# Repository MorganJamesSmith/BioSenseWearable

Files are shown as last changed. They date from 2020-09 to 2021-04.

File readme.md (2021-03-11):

# P21

## Building the Project

The project can be built either with the Makefile in the gcc folder in order to
use the arm-none-eabi-gcc toolchain or with the Segger Embedded Studio project
in the ses folder.

The SES project and Makefile are both configured to build the project for the
nRF52840 Dongle (PCA10059). The Makefile can also be used to build the project 
for the nRF5284-DK (PCA10056) by setting an additional variable when running
make (`make BOARD=BOARD_PCA10056`).

## Programming the Board

If using the Makefile, the board can be programmed through gdb with
`make debug`, which will start and OpenOCD instance and launch a GDB session
conneted to it. To debug the board with a Black Magic Probe, use the `GDB_FILE`
variable to specify the probe's serial port. For example,
`make debug GDB_FILE=/dev/ttyACM0`.

## Licensing

The folder nRF5_SDK_17.0.0 is third-party code subject to its own licenses.

All other intellectual property in this repository (code, hardware designs,
documentation, etc.) is provided under the BSD-3 clause license (SPDX:
BSD-3-Clause https://spdx.org/licenses/BSD-3-Clause.html).

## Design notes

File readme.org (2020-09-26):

#+title: BioSense21

A university project by Morgan Smith, Samuel Dewan, Tadhg
McDonald-Jensen, and Jason Nyentap.
* Description
A wearable device that would contain a suite of sensors intended to
produce enough information to detect illness before symptoms occur.
* Feature List
** User Interface (do we need one?)
- Vibration Motor (for what?)
- A button (for what?)
- Speaker (for what?)
** Necessary Hardware
- Battery (Lithium Ion)
- Charging circuit
- Accelerometer IMU ($11.07) [[https://www.digikey.ca/en/products/detail/tdk-invensense/ICM-20948/6623535][ICM-20948]]
- Heart rate+oximeter
  ($11.77 [[https://www.digikey.ca/en/products/detail/maxim-integrated/MAX86150EFF/7392247][MAX86150EFF]])
  or
  ($3.64 [[https://www.digikey.ca/en/products/detail/osram-opto-semiconductors-inc/SFH-7050/6137020?s=N4IgTCBcDaIMoDEASACA7ABgKwZAXQF8g][SFH 7050]]) ($7.66 [[https://www.mouser.ca/ProductDetail/Maxim-Integrated/MAX32664GWEC%2bT?qs=%252B6g0mu59x7KPYz%252BeYnJYdg%3D%3D][MAX32664GWEC+T]]) ($10.13 [[https://www.mouser.ca/ProductDetail/Maxim-Integrated/MAX32664GTGC%2b?qs=vmHwEFxEFR%252B4L9bBONurNg%3D%3D][MAX86140ENP+T]])
- Body + Ambient temperature ($1.06 [[https://www.digikey.ca/en/products/detail/microchip-technology/TCN75AVUA713/739451][TCN75AVUA713]])
** Possible Sensors
- air quality ($18.39 [[https://www.digikey.ca/en/products/detail/bosch-sensortec/BME680/7401317][BME680]] includes temperature)
- noise levels (microphone)
- Breath rate sensor (how?) (Pulse oximetry?)
- Pulse oximeter/heart rate
- ECG (AD8232)
- UV exposure ($2.48 [[https://www.digikey.ca/en/products/detail/silicon-labs/SI1133-AA00-GMR/5725927][SI1133-AA00-GMR]])
** Need more research Sensors
- Blood sugar monitor
- Blood pressure monitor
* Similar Projects
** [[https://github.com/estherbm/Open-BioBand][Open-BioBand]]
The code is in Spanish (I think)
License: GPL-3
** [[https://www.pine64.org/pinetime/][PineTime]]
| Soc      | Sensors       | Battery |
|----------+---------------+---------|
| nRF52832 | Heart Rate    | 180 mAh |
|          | Accelerometer |         |

** [[https://www.kickstarter.com/projects/gfw/banglejs-the-hackable-smart-watch/description][Bangle.js]]
- This watch is specifically designed to run javascript, gross.

| Soc      | Sensors    | Battery |
|----------+------------+---------|
| nRF52832 | Heart Rate | 350 mAh |

** [[https://github.com/S-March/smarchWatch_PUBLIC][This random dude who made his own smartwatch]]
- More images here: [[https://imgur.com/a/FSBwD3g][link]]

| Soc     | Sensors       | Battery |
|---------+---------------+---------|
| DA14683 | Accelerometer |         |
* Available drivers and algorithms
https://www.owear.org/open-algorithms
* Studies on early sickness detection
** Currently happening
*** [[https://osher.ucsf.edu/research/current-research-studies/tempredict][TemPredict]]
Using the Oura Ring which is a wearable device that measures heart
rate, inter-beat interval and changes in dermal temperature and is
associated with a smartphone app.
*** [[https://innovations.stanford.edu/wearables][Stanford]]
For iOS users, we support: Fitbit devices, Garmin devices, Samsung Galaxy Watch, Apple Watch, Oura Ring.

For Android users, we support Fitbit devices.
*** [[https://detectstudy.org/][Detect Health Study]]
** Completed
*** [[https://doi.org/10.1016/S2589-7500(19)30222-5][Harnessing wearable device data to improve state-level real-time surveillance of influenza-like illness in the USA: a population-based study]]
References other studies that indicate that increased temperature due
to infection can cause a higher heart rate

Lack of sleep is correlated with an elevated heart rate.

Mentions they would have like to use detection of voice changes or
galvanic skin response to detect stress level to identify
non-infectious causes of elected heart rate.

Heart rate is higher when it's cold and lower when it's warm

Heart rate is higher when you're dehydrated
*** [[https://doi.org/10.1371/journal.pbio.2001402][Digital Health: Tracking Physiomes and Activity Using Wearable Biosensors Reveals Useful Health-Related Information]]
Core temperature decreases during sleep but skin temperature increases

Measurements taken during airline flights differ significantly from
normal measurements

Skin temperature increases from inflammation, and viral disease

Skin temperature increases a lot from Lyme disease

Heart rate increases noticeably when suffering
from Lyme disease or rhinovirus

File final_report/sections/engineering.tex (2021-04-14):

\subsection{Health and Safety}
% {\color{red}
% Using the Health and Safety Guide posted on the course webpage, students will 
% use this section to explain how they addressed the issues of safety and health 
% in the system that they built for their project.
% }
Due to Covid restrictions all electrical work was performed without supervision.  
Since all electrical work uses USB power of 5V no risk of serious injury was possible.
To mitigate risk of shock, it was ensured that work area is clear and that there are no live wires exposed while the board is connected to the power source.
All soldering was performed within reasonable safety guidelines.

\subsection{Engineering Professionalism}
% {\color{red}
% Using their course experience of ECOR 4995 Professional Practice, students 
% should demonstrate how their professional responsibilities were met by the 
% goals of their project and/or during the performance of their project.
% }
% Several aspects of the project were affected by engineering practices
In order to ensure user privacy is maintained, the data collected by the device is only stored locally and
can only be offloaded by USB or SD card (physical access) or over bluetooth using standard bluetooth encryption.
The device is enclosed in a way that ensures that electrical shock is not possible under normal operation.
The bluetooth module we are using is industry canada certified to be safe to use.

\subsection{Project Management}
% {\color{red}
% One of the goals of the engineering project is real experience in working on a 
% long-term team project. Students should explain what project management 
% techniques or processes were used to coordinate, manage and perform their project.
% }
Each member of the team was, due to individual passions, interested in different
aspects of the project, thus division of tasks was organic and did not require a leader or dictating division of work.
Good communication over instant messaging and occasional meetings to discuss updates and re-evaluating
task assignment ensured fair distribution and completion of work.
Though we had created a timeline,
due to underestimating the amount of time certain tasks would take to
accomplish, the timeline had to be pushed back. Working with a group and
deadlines enabled the development of time management skills.

\subsection{Justification of Suitability for Degree Program}

All team members are studying Computer Systems Engineering.  This program
teaches hardware, software, and the intersection between them.  This gave us a
strong foundation for developing our project as an embedded system.  We
applied what we have learned in ELEC and SYSC courses related to embedded
processors to develop our own hardware platform.  This required us to
exercise our electronic circuit analysis skills using concepts like Ohms law or
Kirchhoff’s voltage and current laws to make sure our electronics work
properly.  In order to connect all of our sensors and interfaces to the
embedded processor we used what we have learned about microcontroller
peripherals such as UART, I2C, SPI, GPIO, and timer modules.  In addition to 
creating our own hardware, we wrote software that runs on the embedded processor
to control the device.  The C programming language was used to do this, and we 
applied much of the knowledge and techniques learned from several SYSC courses.  
This includes concepts like interrupts, managing multiple tasks and events, 
using the hardware features of the embedded processor and more.  Some of the
non-technical courses included in the Computer Systems Engineering program have 
also proved useful for managing the project and writing reports. 
% this final sentence is weird.
Since we 
have applied large portions of the knowledge gained from our studies to
our project we believe the project is relevant to what we have studied and 
relevant to our degree program.
% due to the previous courses taken by members of the group, we feel as though we can apply our theoretical knowledge to a practical application more efficiently

\subsection{Individual Contributions}
In this section, the contributions of each group member to the project are
presented. The contributions are divided into those related to the project 
itself, and secondly those related to the writing of this report.

\subsubsection{Project Contributions}
The list below details the contributions of each group member towards the
implementation and testing of the project. In cases where components were 
shared by group members, percentages are given.

\begin{itemize}
    \item Hardware component research and selection - Jason 50\%, Sam 50\%
    \item Electronic prototyping - Jason
    \item Schematic capture - Jason 80\%, Sam 20\%
    \item PCB layout - Jason
    \item PCB assembly - Sam
    \item Hardware Debugging - Sam
    \item Bill of materials and Purchasing - Sam
    \item Command line interface - Sam
    \item USB driver - Sam
    \item Analog interface code - Sam
    \item ICM 20948 IMU driver - Sam
    \item Data logging and file systems - Sam
    \item Bluetooth driver - Jason
    \item Bluetooth interface for companion software - Jason 60\%, Tadhg 40\%
    \item Companion app CLI interactions and usb connection - Tadhg
    \item log file parsing and plotting - Tadhg
    \item Companion app automated testing - Tadhg
    \item Enclosure design - Morgan
    \item Enclosure fabrication - Morgan
    \item MAX86150 PPG/ECG driver - Morgan
    \item Guix package - Morgan
    \item SI1133 UV light sensor driver - Tadhg
\end{itemize}

\subsubsection{Report Contributions}
The list below details the contributions of each group member towards this final
report. In cases where sections were shared by group members, percentages are
given.

\begin{itemize}
    \item 0 Abstract - Morgan
    \item 1.0 Introduction - Morgan 60\%, Jason 30\%, Tadhg 10\%
    \item 1.1 Motivation - Morgan 50\%, Tadhg 50\%
    \item 1.2 Problem Statement - Jason
    \item 1.3 Solution - Tadhg
    \item 1.4 Accomplishments - Morgan
    \item 1.5 Report Structure - Tadhg
    \item 2.1 Health and Safety - Tadhg
    \item 2.2 Engineering Professionalism - Tadhg
    \item 2.3 Project Management - Tadhg
    \item 2.4 Justification of Suitability for Degree Program - Jason
    \item 3 State of the Art - Jason
    \item 4.1 Component Selection - Sam 80\%, Jason 20\%
    \item 4.2 Schematic - Jason
    \item 4.3 PCB Layout - Jason
    \item 4.4 Enclosure - Morgan
    \item 5 Software Implementation Description - Sam
    \item 5.4.1 USB - Sam
    \item 5.4.2 Bluetooth - Jason
    \item 5.4.3 Heart Rate - Morgan
    \item 6.1 Integration Testing - Sam
    \item 6.2 Performance Measurements - Sam
    \item 6.3 Power Measurements - Jason
    \item 6.4 Companion App Testing - Tadhg
    \item 6.5 Physical Dimensions - Morgan
    \item 6.6 Cost - Sam
    \item 7.1.1 Power and Battery Design Challenges - Jason
    \item 7.1.2 Assembly and Parts Availability Challenges - Sam
    \item 7.2.1 Toolchain and nRF5 SDK Challenges - Sam
    \item 7.2.2 USB and Bluetooth Integration Challenges - Jason
    \item 8 Timeline - Morgan
    \item 9 Conclusion - Tadhg
\end{itemize}

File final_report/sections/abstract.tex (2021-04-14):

Early detection of illness could limit the spread of infection, save lives, and
save money.  One possible method of early detection is to continuously measure
someones physiological state.  Here we detail our creation of such a continuous
biometric measurement device.  The device is in the form factor of a watch and
contains sensors to measure skin temperature, ambient temperature, motion, 
heart rate, pulse oximetry, and UV light. The software drivers for UV light,
heart rate and pulse oximetry were not completed in time so data is only
recorded from motion and temperature sensors. The PCB also supports an air
quality sensor which was never populated due to a lack of availability.
The device is powered by a lithium ion battery that is charged
through a USB port and lasts two days of normal operation.  
The total cost of the unit is \costofboard.  Sensor data can be
obtained through the SD card, USB port, or Bluetooth by using the appropriate companion
software.  The companion software can then produce graphs to display the output
of the sensors.  The focus of this solution is on the collection of biometrics
and making them available for analysis.  No attempt was made to perform medical
analysis or give clinical diagnosis from the collected biometrics.  Our
intention was to design an open source system so that those applications could be
integrated with or built on top of the work we have done for this project.

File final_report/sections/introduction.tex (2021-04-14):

This report details the design and creation of a continuous biometric measurement
device costing a total of \costofboard. This device takes measurements from the user
and prepares them for analysis to detect illness or otherwise track well being.

Traditionally, people only seek treatment for ailments after they start
experiencing symptoms; however, it is often desirable to take action before
symptoms appear.  One solution to catch illness earlier could be to monitor a
person's physiological state using various sensors and take action when the
state falls outside of a known healthy state.

Wearables are capable of revealing personal daily physiological cycles with
respect to skin temperature, and heart rate with high accuracy 
\cite{Schuurmans2020}. By comparing a person's current physiological
state with the expected state, it is possible to predict illness with greater
sensitivity than a self diagnosis \cite{POON2014543}. 
One specific example is a study was able to detect a
period of inflammation (confirmed by a medical high-sensitivity C-reactive
protein test) using a participant's heart rate even though the participant
themselves experienced no symptoms \cite{Wearable-tracking2017}.  The same
study even helped a participant get treatment of Lyme disease before the
``Bull's eye'' rash appeared (a common symptom during the early stages of Lyme
disease) by detecting an abnormality in their SpO\textsubscript{2} levels.

Wearable data can also be used to detect group illness rates.  By using heart
rate data and sleep data from fitbit devices and cross referencing that data
with the Centers for Disease Control and Prevention's (CDC) Influenza Like
Illness (ILI) data, a study was able to predict illness 6.3\% to 32.9\% better
than previous methods \cite{Radin2020}.

A survey on health sensing wearables showed that physiological data collected 
over longer periods of time can be useful for gait analysis and activity 
quantification, among other things \cite{Song2014}. Gait analysis is useful for 
patient mobility evaluation in hospitals, can help diagnose some diseases, and 
can also be used as a more general indicator of health \cite{Song2014}. Activity
quantification is import to aid patients undergoing rehabilitation \cite{Song2014}.

Wearables can also detect more immediate dangers to someone's health like a
heart attack \cite{heart-attack}, a fall \cite{Khojasteh_2018}, or dangerously
low or high heart rates.  This information could be used to alert emergency
services to save lives.

In addition to collecting physiological data, many wearables can also measure
environmental data and positional data \cite{Seneviratne2017}. This data has 
proven useful in dangerous work environments such as those commonly 
found in the mining industry \cite{Mardonova2018}. Air quality information can
help miners avoid inhaling hazardous gasses or respirable silica dust 
\cite{Mardonova2018}. Some wearables will even detect when equipment operators
are becoming sleepy and warn them that it is no longer safe to continue working
\cite{Mardonova2018}. In the construction industry, there is a high rate of 
severe contact injuries \cite{Awolusi2018}. The use of location data can help 
reduce these contact injuries by preventing workers from entering dangerous 
areas or coming into contact with equipment \cite{Awolusi2018}. Wearable devices
capable of measuring both physiological data and elevation can be used to detect
altitude sickness, which can occur when unacclimated individuals experience sudden 
changes in elevation \cite{Muza2018}. These sudden changes in elevation are 
possible while driving, riding a train, flying, or taking a cable car up a mountain 
\cite{Muza2018}.

\subsection{Motivation}

Despite all of the advances in medical technology, a cure for diseases and
allowing humans to live longer are ever present goals for scientists and 
doctors alike.  Often wide spread diseases we have not prepared for can occur in
society.  COVID-19 is a pandemic that
has, at the time of writing, claimed an estimated 3 million lives globally
\cite{johns-hopkins-corona-chan}, and continues to infect more people every
day.  In 2007 it was estimated that the total cost of occupational illnesses
among civilians in the United States was \$58 billion \cite{Leigh2011}.
Slowing the spread of disease could save lives and save money.

One method of limiting the spread of disease is early diagnosis.  This would
allow individuals who are aware they are ill to take measures to reduce the
spread of their illness, even before symptoms manifest.  This will be
particularly useful for healthcare providers who work with high risk
individuals, since identifying symptoms early has the highest efficiency for
protecting others.

By creating a personal physiological profile and constantly
comparing the user's current physiological state to it, illness can be detected
early.  The motivation for our project is to create a device capable of measuring 
enough of the user's current physiological state to predict illness.  This is done 
in the hope that it could be used to slow the spread of illness's and, to speed
recovery from illness's by starting treatment earlier.

\subsection{Problem Statement}

One way to facilitate early diagnosis is to periodically measure biometrics on 
patients and make clinical diagnoses based on patterns or changes in the 
measurements. A convenient and low-cost method to collect and log biometric data 
is needed in order to make the potential benefits of the technology available to 
a large number of people. Wearable devices are well suited to this application 
because they have continuous access to the user’s biometric data as long as the 
device is being worn, and they do not require any input from the user to perform 
most, if not all, measurements. This means that a wearable device can take as 
many measurements as it needs, whenever it needs to, in order to create useful 
data logs that describe the user’s biometrics and perhaps their environment at 
the time the measurements were taken.  This information may then be used to 
detect abnormalities in the user’s physiology and could be used to aid in the 
early detection of illness. The objective of this project therefore, is to 
create a wearable device that can measure a variety of critical health metrics 
including skin temperature and heart rate.

\subsection{Solution}

The solution provided by this project is a wrist mounted wearable health 
monitoring device. The device provides a sensor platform that is suitable for 
early detection of disease. The included sensors can measure skin temperature, 
ambient temperature, motion, heart rate, pulse oximetry, UV light, and air quality.  
The electronic components fit into a comfortable, wearable 3D printed plastic enclosure.
The device is powered by a lithium polymer battery which can be recharged
through the USB-C connector.  The final cost of the full device ends up being \costofboard.

The wearable device has limited user interfaces consisting of an indicator
LED for power, notifications, and debugging. It also features a power button
to turn the device on and off. The main interactions with the device occur 
through a companion software that connects to the device through Bluetooth or 
USB. It is limited to simply receiving and decoding data received from the 
wearable device, and exporting it in an analyzable format such as a csv or json 
file.

The device stores the collected sensor information to a micro SD card
in the device which is then read back when requested via the companion software.
The SD card is replaceable, and the capacity of the card used will dictate
how long the device can record data before needing to off load to the companion
software.

The focus of this solution is on the collection of biometrics and making them
available for analysis. No attempt was made to perform medical analysis
or give clinical diagnosis from the collected biometrics. Our intention was to
design the system so that those applications could be integrated with or built
on top of the work we have done for this project.

%Should this be in a reflection or something? Not really part of a solution,
%it is a disclaimer.

%In order to reduce development cost and complexity, the hardware component of
%the project uses sensors that are readily available from online sources, and 
%that can be assembled on a PCB by hand relatively easily. As a result the 
%selection of sensors may be more limited or lower quality than what is possible 
%if options that are made to order, or only available in large quantities had been
%explored.  The use of parts that can be soldered to a PCB without paying for
%the services of an advanced manufacturing facility also resulted in the final 
%hardware design being larger than it would have been otherwise.

\subsection{Accomplishments}

Our team successfully created a wrist mounted wearable health monitoring device
that is capable of measuring skin temperature, ambient temperature, and motion.
The hardware for heart rate, pulse oximetry, and UV light sensors are in place
however the software drivers were not completed in time. 
The air quality sensor was never available so the driver was not started and was
never populated on the PCB. The hardware is fully functional and correctly
connects all the selected components together.  The software is able to connect
the device to companion software located on a separate device using Bluetooth
and USB.  We are able to log motion and temperature sensor to the SD Card.

\subsection{Report Structure}
Subsequent sections of this
report cover the hardware and software design of the project in detail, as well
as discuss some of the challenges that were faced in pursuing the solution
outlined here. Information regarding the tests performed on the final project
are also detailed in this report, and a series of appendices are included with
visuals to show some interesting parts of the design and what the final product
looks like.

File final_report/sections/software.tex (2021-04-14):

We have split our firmware into a number of separate modules, as shown in figure
\ref{fig:fw_block_diag}. All of the drivers for microcontroller peripherals
such as serial interfaces and the ADC are provided by the nRF52 SDK, which is a
library provided by Nordic Semiconductor, the manufacturer of the nRF52840
microcontroller we are using. We are also using some higher level components
from the nRF52 SDK such as the USB CDC-ACM stack, a FAT32 filesystem driver and
Nordic's soft device S140 which is a Bluetooth LE peripheral stack.

These third party components are be used by the software we wrote ourselves
which includes the drivers for all of our sensors (IMU, optical heart rate
sensor, air quality sensor and UV light sensor) as well as the signal processing
code required to derive a heart rate from the raw data we receive from our
optical heart rate sensor.

At the application layer we have three modules. Our data logging service is
responsible for most of the operation of our device and continually collects
and logs sensor data. The Bluetooth data transfer service facilitates accessing
the logged data over a Bluetooth interface. Our debugging interface exposes our
firmware functionality over a USB serial interface so that integration tests can
be run on the microcontroller.

\begin{figure}[!htb]
\centering
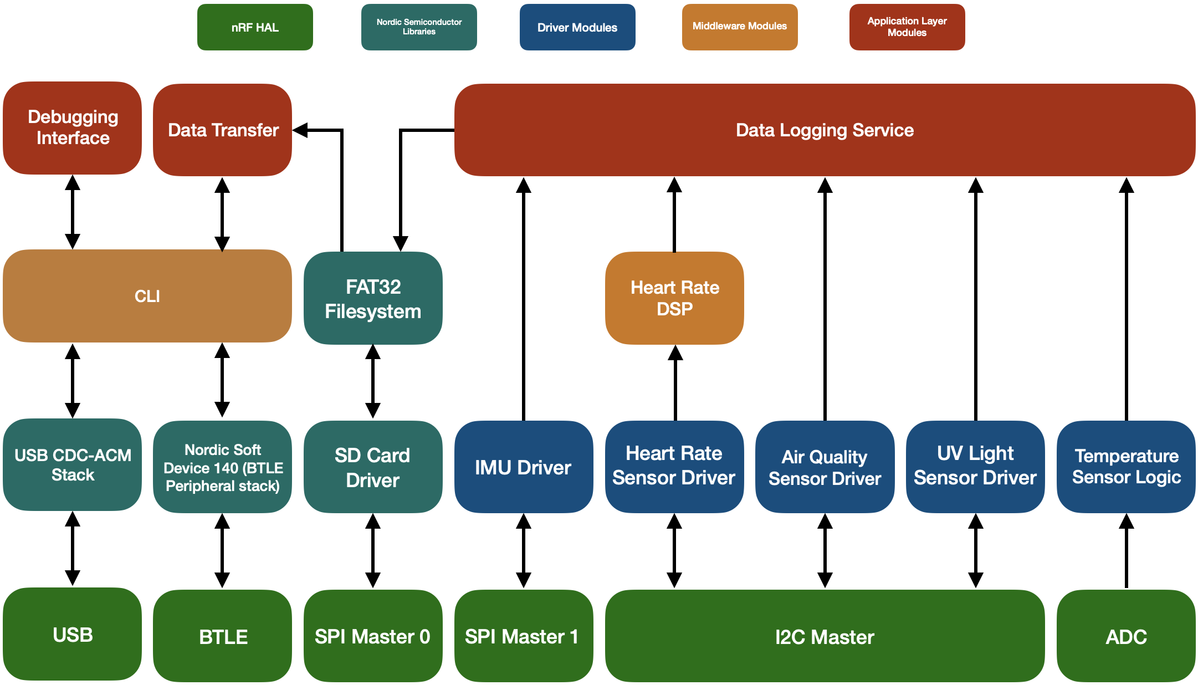
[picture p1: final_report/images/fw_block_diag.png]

\caption{Firmware block diagram.}
\label{fig:fw_block_diag}
\end{figure}

\subsection{Super Loop}

We chose to use a super loop architecture for our firmware because we predicted
that the approach would be sufficient for our needs and would be easier for us
to implement then making use of a realtime operating system. Our firmware
consists of an initialization section followed by an infinite main loop.

Our code is separated in to a number of software modules (as shown in figure
\ref{fig:fw_block_diag}). The software modules that we wrote have an
initialization function which is called once on system startup. Some of our
firmware modules are entirely interrupt based, but many have a service function
which is run in each iteration of the main loop.

Figure \ref{fig:fw_flow} shows the flow of our firmware. We start with a number
of initialization tasks before starting to loop through the service functions
for our modules. Each service function will check if there is any work to be
done for a specific module and start tasks that are ready to begin. After
each iteration of the main loop the wait for interrupt instruction is used to
cause the processor to enter a sleep mode until an interrupt occurs. We have a
timer configured to generate interrupts every millisecond to increment a count
which is used as a time reference throughout the firmware, because of this the
processor will sleep for at most one millisecond at a time.

\begin{figure}[!htb]
\centering
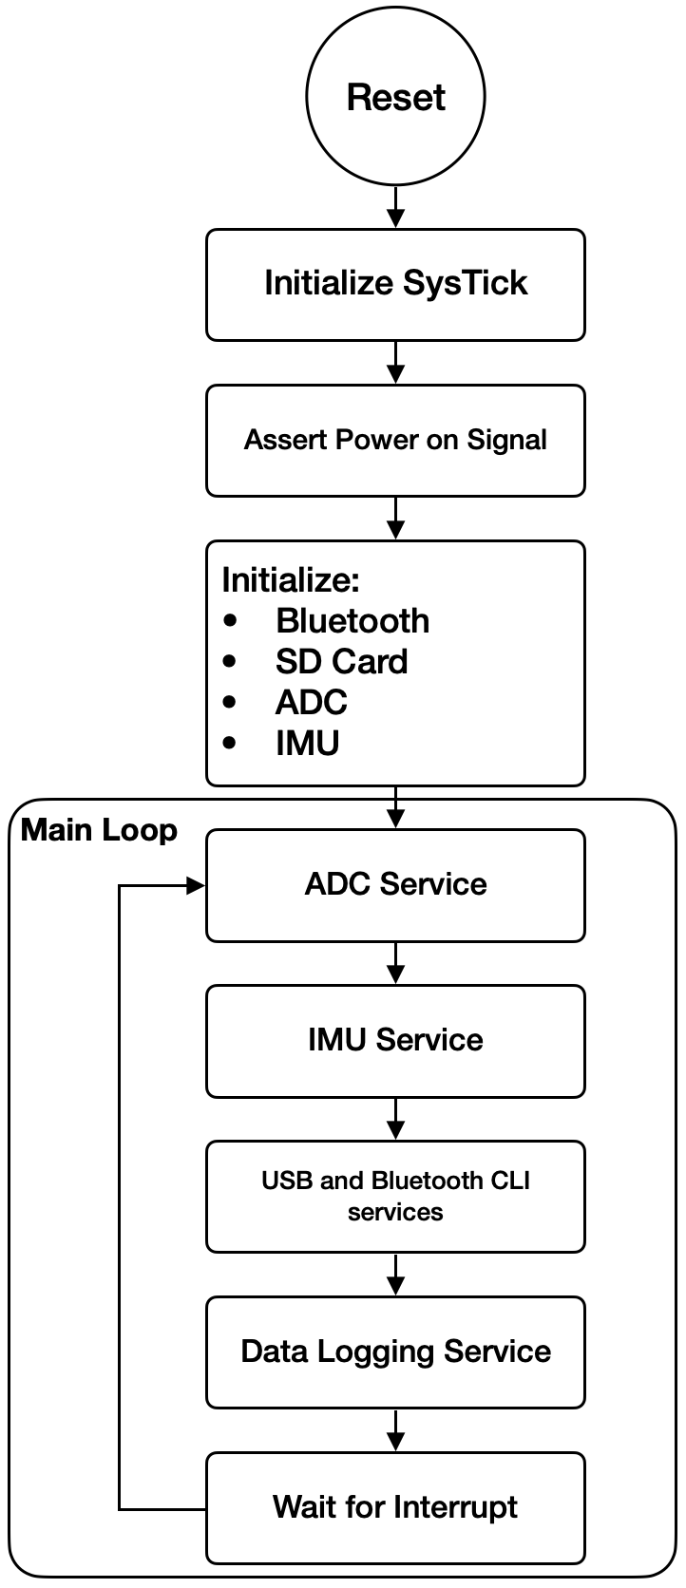
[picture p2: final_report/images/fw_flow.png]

\caption{Firmware flow chart.}
\label{fig:fw_flow}
\end{figure}

The super loop architecture is a cooperative multitasking system. This makes it
important that the service functions which are called in the main loop do not
block for long periods. If a service function was to block it would prevent the
other software modules on the system from operating correctly. In order to meet
this requirement our service functions are written as state machines. Modules
keep track of their current state and are able to determine what, if anything,
needs to be done in each iteration of the main loop based on their state.

We were not able to completely avoid blocking in the main loop because of our
use of a third party FAT filesystem implementation. The filesystem implementation
blocks while writing to the SD card. The performance implication of this are
discussed in section \ref{subsec:testing-data-logging}.

\subsection{Interrupts and Bluetooth Soft Device}

Our firmware makes use of a bluetooth stack provided by Nordic Semiconductor
know as the S140 Soft Device. This "soft device" is distributed as a binary
blob which is flashed to the microcontroller separately from the application
software. The soft device takes ownership of number of microcontroller
peripherals including the radio hardware, clock and power management peripherals,
multiple timers, non-volatile memory controller and cryptography accelerators.
The soft device schedules itself independently of the application using one of
the microcontroller's real time clocks and application software interacts with
the soft device using supervisor calls.

All interrupts are received by a piece of code called the master boot record
(MBR). The MBR then forwards them to the soft device if there is one installed
on the microcontroller. The soft device uses some interrupts for its own
purposes, and interrupts which the soft device does not use are forwarded to the
application. Nordic Semiconductor specifies that this forwarding process adds
less than three microseconds of latency to peripheral interrupts which are to
handled by the application.

Figure \ref{fig:fw_int_prio} shows the interrupt priorities used in our system.
The priority levels shown in red are reserved by the soft device bluetooth
stack, those shown in blue are available for use by application software. The
soft device uses the highest interrupt priority level for its timing critical
interrupts. The second highest interrupt priority level is reserved for the
soft device's peripheral access control fault handler so that the soft device
can safely handle any faults which are caused by application interrupts. The
soft device also used priority level four for API calls and processing tasks
that are not time critical.

\begin{figure}[!htb]
\centering
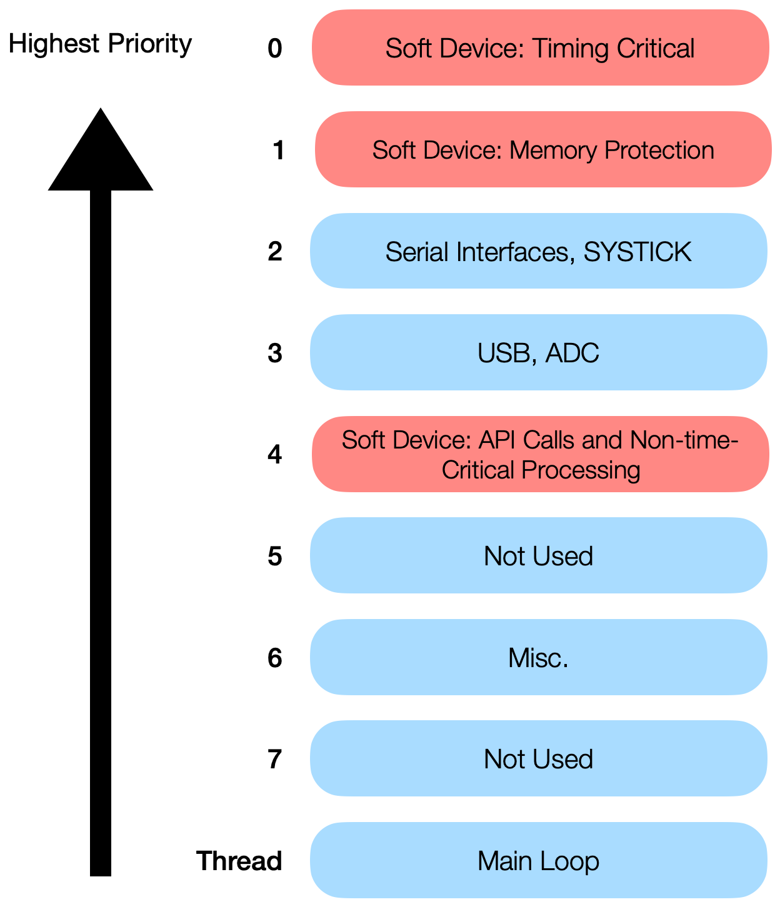
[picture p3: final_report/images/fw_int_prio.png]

\caption{Interrupt priorities.}
\label{fig:fw_int_prio}
\end{figure}

Most of our application interrupts are configured at priority levels two and
three. Our interrupts are grouped into SysTick and and serial interface
interrupts at priority two and USB and ADC interrupts at priority three.

The priority two interrupts are those which we expect to be very short. The
SysTick interrupt is at a high priority to avoid help avoid jitter in our system
time and the serial interrupts are placed at priority two to achieve the best
possible serial interface performance.

\subsection{Data Logging}

The core of our firmware is the data logging service. Sensor drivers push data
to this software module which is buffered and then later stored to the SD card
using the FAT filesystem. The data logging module has two 512 byte buffers. The
module fills one buffer, then writes it to the SD card as it begins to fill the
other.

Figure \ref{fig:fw_data_flow} illustrates the flow of data through the data
logging service. Each sensor driver pushes data to the data logging service at a
rate selected based on the type of data that the sensor produces. Every sample
of sensor data is wrapped in a header that indicates the current system time
when the value was collected, the type of data, and the length of the data.
The resulting packet is then added to the data logging service buffer. Approximately
once per second the data logging buffer will be written to the SD card using the
filesystem driver.

\begin{figure}[!htb]
\centering
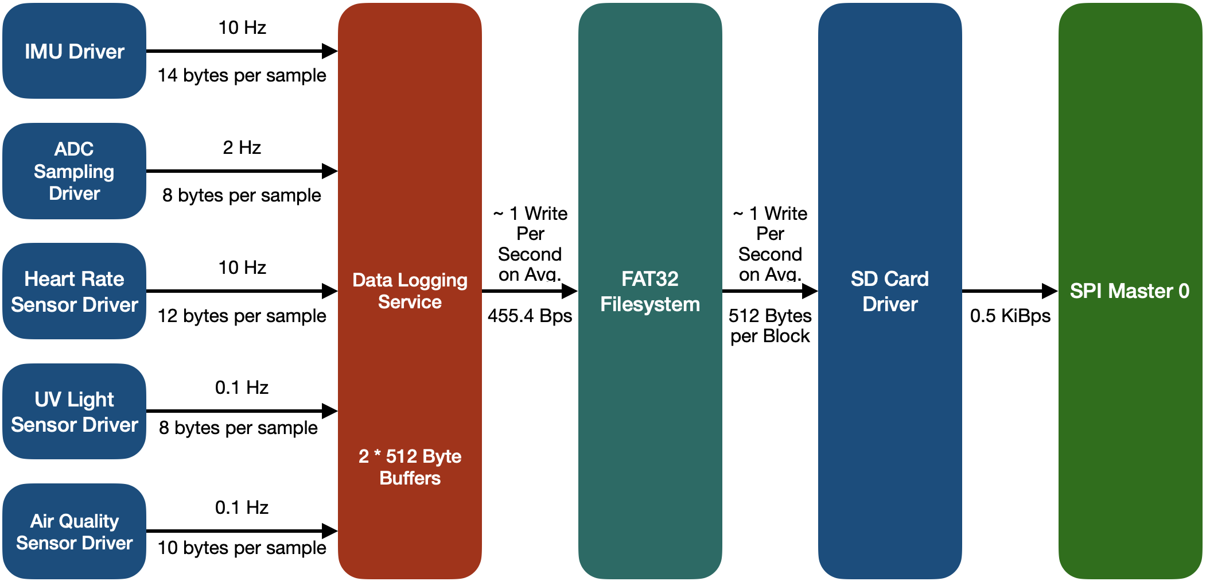
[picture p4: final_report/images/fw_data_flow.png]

\caption{Data flow.}
\label{fig:fw_data_flow}
\end{figure}

\subsection{Drivers}

\subsubsection{USB}

The USB serial interface software module provides a simple abstraction over the
nRF5 SDK's USB communications device class abstract communications model
(CDC-ACM) driver which allows for serial port emulation. The USB serial module
maintains circular buffers for input and output and provides a variety of
functions for reading from and writing to the buffers. The output buffer can be
written to in a blocking or non-blocking fashion. The input buffer can be read
character by character, in blocks, or by line with a selectable delimiter.

\subsubsection{Bluetooth}

The design goal for the Bluetooth driver was to have it behave like a serial
port in the same fashion that USB CDC does. Our intention in doing this was to 
simplify the design of the companion software as well as the command line 
interface present on the microcontroller. This goal was fully achieved 
on the microcontroller side of the communication link. The software interface for 
Bluetooth was made identical to USB so that they can be used interchangeably 
without additional complications. On the PC side where the companion software
runs the solution was not as elegant. We had hoped to find a way to make the
Bluetooth connection appear as a serial port so it could be used interchangeably
with the USB CDC connection, but a method to do this was not found. It likely
could be done by writing custom drivers, but this was outside the scope of the
project. Instead, a cross platform Python library was used to establish the
Bluetooth connection to the device and communicate with it as you normally
would with a Bluetooth device.

The device uses Bluetooth Low Energy, which works by advertising
available services to other nearby devices. Each service may offer a number
of characteristics that can be read only, write only, read-write, and have 
several other options such as notifying a connected device when a characteristic
value changes. The Bluetooth Low Energy specification includes descriptions of several
standard services and their characteristics, but none of these could be used to
to achieve the serial port-like behaviour needed for this project. A custom
serial port service included with the Nordic SDK was used instead. This service
has two characteristics, one named TX and one named RX. The RX characteristic is
write only and is used to send data to the device. The TX characteristic is
written to only by the device and has notifications enabled. If a connected device
wants to receive data then it must subscribe to the notifications of the TX 
characteristic. This solution worked out quite well, although it has a low 
throughput in comparison to USB. The fact that each notification packet can only 
hold approximately 20 bytes and must be acknowledged before the next one is 
sent likely contributes to the low throughput significantly. It was not expected
that Bluetooth Low Energy would be very fast however, since it is optimized for 
power consumption instead of speed. This trade-off is well suited to this project 
because it is battery powered.

\subsubsection{Heart Rate Sensor}

Our heart rate driver is based on an open source implementation written in
C++ \cite{max86150-ardino}. Since the SDK we are using falls under the nRF5
Nordic License, only software that is compatible with this license can be
integrated into the project. The open source C++ heart rate driver is under the
expat license so we are free to use it as long as the copyright notice is
maintained. Unfortunately, not all useful open source software was licensed in
a way compatible with the SDK license. In particular, it would have been ideal
to reuse an algorithm to convert raw PPG data to beats per minute, however the
available algorithm was licensed with the Lesser GNU Public
License \cite{wasp-os} which is incompatible with the SDK license.

\subsubsection{Inertial Measurement Unit}

Our driver for the ICM 20948 IMU is written from scratch. The driver is a finite
state machine that makes use of the nRF5 SDK's SPI driver. The state machine
controls the process of initializing the sensor and of periodically taking
readings, which are then handed off to the data logging service to be recorded.

A simplified state diagram for the IMU driver is shown in figure
\ref{fig:fw_imu_fsm}.

\begin{figure}[!htb]
\centering
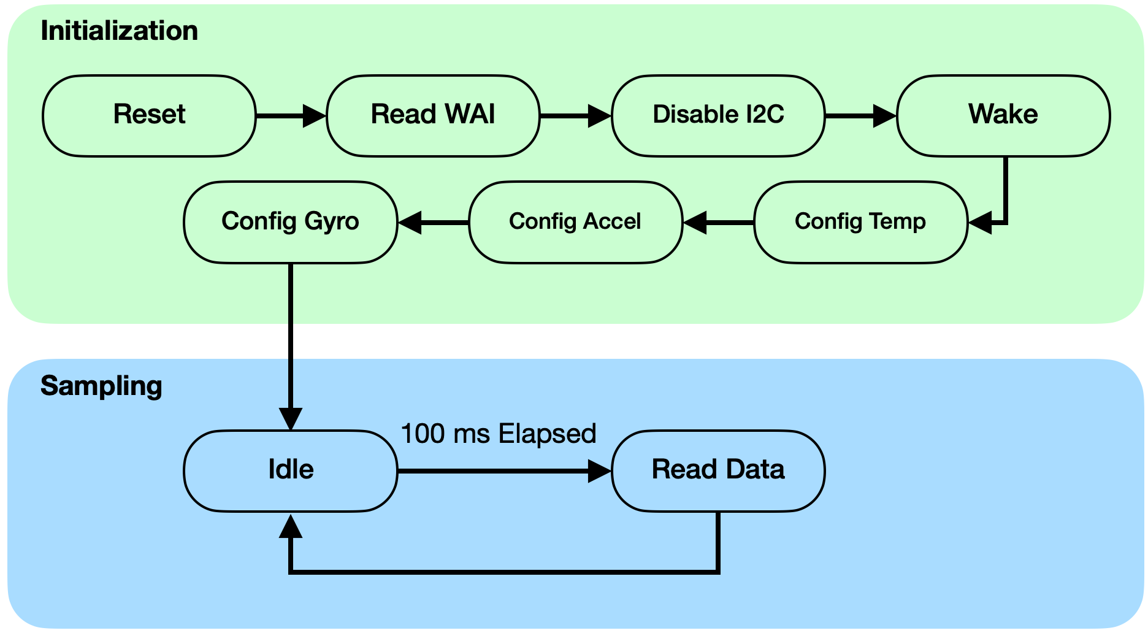
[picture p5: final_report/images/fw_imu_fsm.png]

\caption{IMU driver state machine.}
\label{fig:fw_imu_fsm}
\end{figure}

\subsection{Command Line Interface}

Our firmware provides a command line interface (CLI) which is available via the
USB or bluetooth serial interfaces. This command line interface is used for
debugging, testing and for interaction with the companion app. Our CLI
abstraction provides an identical interface over USB or bluetooth.

The CLI provides a number of commands which are intended for human interaction
including commands for printing out sensor data, accessing profiling information,
writing test messages to the SD card and reading directories and files from the
SD card.

The CLI also has a number of commands which are intended to interact with our
companion software. These functions allow the companion software to read files
from the SD card. The files are written out over the serial interface in
hexadecimal format.

\subsection{Companion App}

The companion app is a desktop application written in python to connect to the device, extract the log data and convert it into a plain text format convenient for further analysis.

Since during development there were a number of things that were likely to change or unknown, the companion software was designed to be highly modular so that each part was isolated for sake of testing and updating.  The flow of data is described by \ref{fig:companion_app}

\begin{figure}[!htb]
    \centering
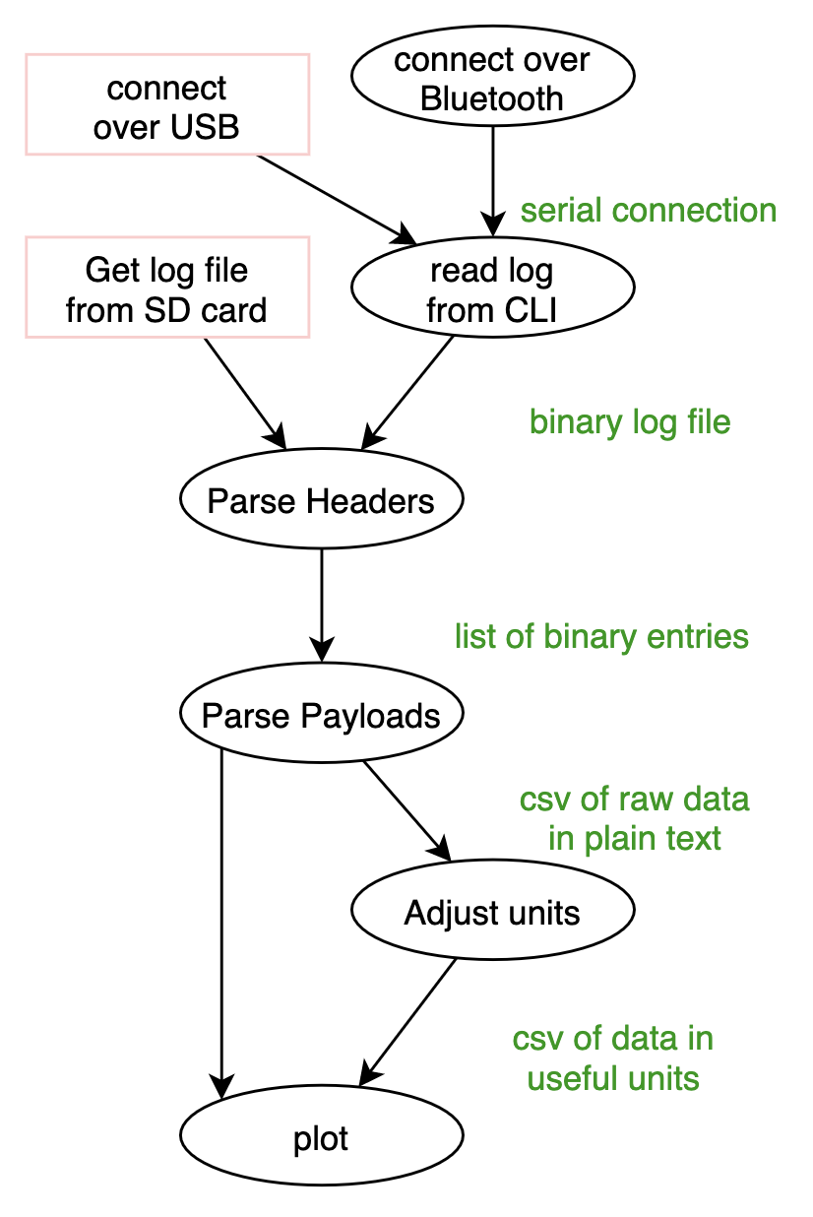
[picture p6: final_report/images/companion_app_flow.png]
    
    \caption{Companion app flow diagram}
    \label{fig:companion_app}
\end{figure}

\subsubsection{Extracting log file}

When the device is connected over USB the companion software can be run to open a serial connection with the device, otherwise the companion software will scan for the device over bluetooth and attempt to pair and connect.  Once a bluetooth connection is established a wrapper is created to emulate the same behaviour as a serial connection so that the CLI communication module can use both connections interchangeably.

The interaction with the CLI consists of sending a time alignment command and using 'hcat' command to read the offset file and log file.  

Since the device does not have time keeping all log entries are recorded with internal timestamps only, the time alignment command creates a log entry matching an internal timestamp with a unix timestamp generated by the companion app.  

The log file consists of binary data blobs with variable length so identifying the boundaries of entries from the middle of the file is impossible without additional context, for this reason a separate file is kept with a list of offsets corresponding to each reset so an option can enable only recording data from a given reset index.

\subsubsection{Parsing log file}

Once the log file is obtained either by extracting it through the CLI interface or by extracting it from the SD card directly, it is converted from a binary format into plain text CSV files for each type of entry.

The module which parses the headers will read the length of each entry's payload and ensure the correct length of bytes is being read.  Particularly if an entry is only partially written when the device loses power a reset index specified by the separate file will indicate this and the partial entry can be discarded without corrupting all subsequent data.

The module which parses the payloads relies on introspection and struct definitions for each entry type.  The order and types of the fields are used to extract data from the log file while the name of the struct defines the name of the csv file created and the variable names in the struct are used to generate a header for the csv.  This way adding a new sensor requires only adding a struct and no additional parsing code is needed.

Unit adjustment was accounted for in the original plan however since all log entries are adjusted on the device to be fixed power of 10 of a useful unit (for example accelerometer data is $10^{-4} g$ where $g$ is a standard gravity unit) the companion app doesn't do additional adjustments. 

Some additional code is used to create a graph of a selected csv file for demonstration purposes, this also can produce live updating graphs

% TODO: talk more about live updating stuff?
% what else did I miss?

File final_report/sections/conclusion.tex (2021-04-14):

Our project provides an open source and open hardware platform for monitoring physiological signals.
It is designed to be expandable and re-usable so that changing the suite of sensors would require
very little modification of the work we performed.

If the project was to continue we would finish the drivers for UV light, heart rate and pulse oximetry.
A natural extension to the project would be to extend the use of data after collection, 
analyzing the data for illness.
Also possibly create a companion app which runs on a smartphone or other device
that would be more portable so that data could be pulled from the device more often
for the user's information.

We believe that open source wearables are likely to grow in popularity in the future due to
concerns with how large corporations deal with user privacy. The PineTime is an
open source wearable that is currently picking
up steam and more open source wearables are likely on the way.

We're happy to put our design out publicly for others to use and we hope some
good comes of it.

\subsection{Reflections}

This section contains reflections for each group member. These reflections
discuss how each group member felt the project went, and what they would do
different if they had to do it over again.

\subsubsection{Sam}

From my perspective I think that our project went fairly well, but that we
probably should have limited our scope further. Our hardware design and assembly
went relatively smoothly. There were a couple minor issues that could have been
fixed if our timeline allowed for a second PCB revision and we ended up having
to leave off some parts (such as the BME680 air quality sensor) and find
substitutions for others due to availability issues, but in general I am happy
with how our hardware turned out. Our software did not turn out as well, we
were slow to get started with the proper toolchain and SDK for the
microcontroller we choice to use and ended up spending much of our development
time learning to use the nRF5 SDK rather than writing our own application
software.

I think that we could have made a stronger push into software development
earlier, which may have helped with some of the software issues we ended up
with. We could also have prioritized choosing a microcontroller that we were
more familiar with over picking one with integrated Bluetooth. Instead, we could
have used a separate Bluetooth module or relied solely on USB for data transfer.
Using a microcontroller that we had previous experience with would likely have
allowed us to move much more quickly on software development.

I also think that we should have foreseen the issues we had with obtaining the
components that we used in our design, which were likely related to the widely
reported electronics supply chain shortages due to the ongoing pandemic. We
initially ordered only enough of most of the components we used for a single
copy of the board since we were worried about wasting our budget if it turned
out that our board design had problems and need to be changed before we
assembled the second copy. In retrospect we probably didn't have time for a new
PCB revision anyways, and even if we had designed a second revision it is very
unlikely that we would have made changes as large as replacing any of the major
components. We should have ordered enough components for two copies of the
board right away to ensure that we purchased all of the parts we needed when
they were available.

\subsubsection{Tadhg}

Our project was quite ambitious from the beginning and early on we had intended to have 
well established fallback plans to cut out parts of the initial design to save on time,
however I think that ended up getting lost before the first proposal was done so there wasn't
as clear a plan when things started to be delayed.

Of the group I have the least amount of experience with hardware or programming in low level
languages, my expertise is more in high level software or in software architectural design.
I had anticipated working closely with teammates to quickly pick up on the skills needed to 
write the software drivers but had not anticipated how difficult that would be with the pandemic
restrictions.  Because I wasn't regularly interacting with my peers as I would have from in person
classes I made far too little progress for the first term of the project and had a much higher
course load than expected in the second term.  

If I was to redo the project I definitely would be reaching out regularly to get on top of
the required tasks and interacting with the team more. As well as keeping better schedules of my time
instead of relying on deadlines in culearn or "working after the lecture" like I do for other classes.

\subsubsection{Jason}

Overall, I think our project went ok, especially considering how bad it could
have gone. I felt that the project was risky from the start because a large
component of it is hardware design. There was very little room for error in the
board design because we only had time for one revision, manufacturing times
and component availability were out of our control, and simple mistakes in board 
design or assembly could have damaged many components wasting time and money. 
The COVID situation only made things more complex because we lost some of our 
backup plans for board assembly and could not easily work together on hardware 
development, debugging, and testing. All of that being said, I think we did a 
very good job of adapting and overcoming the issues we faced despite the cards 
not being in our favour. I was aware of all of these potential problems going
into the project, but I enjoy hardware development and was confident in our 
abilities so I was willing to take on the risk. What I did not foresee was the
software component of the project lagging behind as much as it did. I had no
worries about the software development at the beginning of the project 
because I thought it was very low risk, but by the end of the project it was
clear that I was wrong. I was not as involved with software development as I was
with hardware development so I am not the best person to say what we should 
have done different, but I think using a microcontroller that at least one of us
was familiar with would have helped. One thing we could have done differently to 
make hardware development much easier would be to make an entirely different 
project that does not depend on obscure sensors. Many of the sensors used in the 
project have little to no alternatives, and they tend to come in small packages 
that are hard to work with. We also could have made it easier by making 
something where size is not as relevant as it is in a watch.

\subsubsection{Morgan}

Our project was quite ambitious, but I feel like we made great progress.
However, there are a few areas I think we fell short in.

We started the software for our project much later than intended.  This
occurred for a few reasons.  We didn't take into account the time needed to
setup and learn the development environment.  The Nordic SDK was more difficult
to setup than expected, and the documentation is quite lackluster.
Furthermore, there was little feedback when writing drivers as we did not have
the hardware yet.  If we had setup a testing framework ahead of time that did
not rely on the hardware, I believe that would have made much more progress
earlier on.

Personally, I wish we had gone with open source drivers for the main board
instead of relying on Nordic's SDK.  Using Nordic's SDK prevented us from
integrating code under the GNU Public License into our project.  It also limits
the licenses we can choose to release our project under.  Furthermore, it is
not well documented.  We decided to use it because we believed it to be the
easiest option.  While that might be true, I dislike the limitations it put on
our project.

I am quite proud of the enclosure and the methods I used to create it.
Traditional 3D modeling programs have given me no end of grief so I decided to
try using OpenSCAD.  This program allowed me to pragmatically tune tolerances,
thicknesses, and positions with ease.  If I had more time, I would investigate
methods to integrate OpenSCAD with KiCad in order to generate parts of the
enclosure based on the electronic design.

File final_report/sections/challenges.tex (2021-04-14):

Several challenges were faced during the course of this project with both the
hardware and software development. This section will describe some of the 
challenges faced, how they were overcome, and what trade-offs or compromises,
if any, had to be considered when finding a solution.

\subsection{Hardware Challenges}

\subsubsection{Power and Battery Design}

One of the major challenges that occurred with the hardware development early
on in the project was the power supply. The original plan as described in the 
proposal was to use a single rechargeable AAA nickel metal hydride (NiMH) 
battery. Designing a power supply to work with the low input voltage of 1.2V 
to 1.0V proved to be quite difficult due to a small selection of components that 
work at that voltage. The most difficult part was trying to implement a soft 
power on / off circuit as well as an automatic switchover circuit to shift the 
electrical load from the battery to USB power. The voltage drop across a diode 
for example makes the resulting signal nearly unusable to turn on a MOSFET. 
Diodes with a very low forward voltage drop and MOSFETS with very low gate 
threshold voltages are available for a higher price, but keeping cost down was 
also a very important goal. In the end a design was created, and since it was 
expected that it may present some problems, it was prototyped on a breadboard 
so that testing could be done before moving ahead with schematic capture and 
PCB design.

Testing showed that the design mostly worked, but had some flaws that were 
deemed unacceptable for this project. The first concern was that the power 
supply would not be able to supply enough current. It was capable of powering 
an nRF52840 development board with some additional resistive load, but it 
struggled to maintain a set voltage and it became apparent that it would be 
barely capable of powering the final design with several sensors. The second 
issue was with voltage regulator start up under load. The switching regulator 
was only able to start with a very small load on it, but once the output had 
reached the desired voltage more load could be placed on it without issue. When 
too much load was attached to the regulator before start up it would stay in an 
under-voltage lockout state indefinitely. This problem may or may not have 
presented itself in a real-world test with the final design, however the goal 
was to have a robust solution that was reliable and not leave things to chance 
with a potential race condition. The final problem was efficiency. With a light 
load the power supply performed in an acceptable fashion, but under heavier 
loads efficiency dropped off much more than expected. The datasheet for the 
regulator did not indicate that efficiency would change appreciably over the 
range of current being drawn for testing, but it did indicate that lower input 
voltages would cause a significant decrease in efficiency. It is believed that 
higher load caused the battery voltage to drop due to its series resistance 
which then caused the regulator to draw much more current to account for the 
higher load and decreased efficiency at the same time because of the decreased 
input voltage. Replacing the battery with a lab power supply set to constant 
voltage showed the expected efficiency under both light and heavy loads. For 
these three reasons it was decided that the original idea of using a single 
rechargeable AAA NiMH battery was not feasible. 

At this point the group had to decide between using two AAA NiMH batteries in 
series to increase the voltage, or starting over and using a LiPo battery. It 
was decided that two AAA batteries would be too large, so the switch to LiPo 
was made and the power supply was subsequently redesigned to reflect these 
changes. One of the design requirements in the proposal was to have the 
batteries removable so they could be swapped out with charged ones instead of 
waiting for the device to charge them. This will no longer be possible with 
the current design; however fast charging capability has now been added as a 
replacement.

\subsubsection{Assembly and Parts Availability}

One of the key challenges that we planned for and managed on the hardware side
of our project was the difficulty of assembling our circuit boards by hand. Due
to the sensors we wanted to use coming in packages designed for small, high
density printed circuit board designs and our desire to build a prototype that
was roughly wrist sized we ended up using a number of components that were not
particularly well suited to hand assembly.

For the most part our assembly still worked out well using a hot air reflow
technique, but we did encounter significant frustration and delay in soldering
our microcontroller module to the board. The module we used was not amenable to
the hot air reflow technique since the pads that needed to be soldered are
located below an RF shielding can. This means that it took a considerable amount
of time and heat to properly reflow the solder paste below the module and we had
inconstant results with no way of properly inspecting the module to ensure that
it had been soldered properly. In the end we simply ended up repeatedly removing
the module and then soldering it back on until we were lucky enough to have all
of the pins flow properly.

An issue that we did not foresee, but should have, was limited availability of
components. When originally designing our hardware we limited ourselves to
components that were readily available in small quantities from online
retailers and that were in stock in large quantities at the time. Between
finalizing our schematic design near the end of the fall semester and ordering
the components for our first copy of the board in the winter semester the IMU
and air quality sensors we had selected had gone out of stock at all of the
electronics retailers that we were familiar with. The IMU later became
available again, but we were never able to obtain the air quality sensor.

A few weeks later when we went to order parts for our second copy of the board
we found that even more components had become unavailable. In addition to the
air quality sensor, the microcontroller module, diodes, USB connector and UV
light sensor that we had chosen for our design were not available. We were
able to find a substitute microcontroller module, though the substitute requires
an external Bluetooth antenna and suitable replacement diodes, but we were
forced to leave the USB connector and UV light sensor unpopulated on the second
copy of our board.

\subsection{Software Challenges}

\subsubsection{Toolchain and nRF5 SDK}
\label{sec:toolchain-issues}

Our toolchain setup ended up being much more difficult than we had envisioned.
In our proposal we had only budgeted ourselves a couple days for this step,
assuming that our experience with other ARM microcontrollers would allow us to
get up and running with the nRF52840 quite quickly. In reality, this seemingly
simple task had required a significant investment of time which held up our
software progress early in the project considerably.

We are used the hardware abstraction layer provided by Nordic
Semiconductor for the nRF52840 as well as some of their libraries. While we had
a build system set up that allowed us to successfully compile and run bare metal
software without any of Nordic's nRF SDK components, actually compiling the SDK 
along with our own code proved to be significantly more challenging. We 
originally tried to adopt our custom Makefile to also compile the nRF52 SDK files 
we required, but ended up having to base our project layout off of one of the 
example projects provided with the nRF52 SDK. A surprising amount of work was 
required to get the Makefile and Segger Embedded Studio project from the example 
to work in our repository without having to place all of our code in the examples 
folder inside the nRF52 SDK's directory structure. The makefiles provided in the
nRF52 SDK are inflexible and make use of a large number of hard coded paths.

\subsubsection{USB and Bluetooth Integration}

One of the challenges faced during integration testing was a conflict between 
the USB and Bluetooth drivers. The two drivers were developed independently of
each other, and both worked on their own. When running the two drivers together
Bluetooth would function as expected but USB would fail to enumerate on the host
and therefore, not work at all. Oddly, this problem would not occur when the 
microcontroller was running in debug mode, it presented itself only in the 
normal run mode. This made the problem much more difficult to solve because
stepping though code, breakpoints, or any other debugging capabilities were not
available outside of debug mode. The alternative technique used was to turn on 
an LED when execution reached a certain point or some condition was met. 

In the end, the solution to the problem ended up being very easy to implement 
despite taking a significant amount of time to find. When Bluetooth is 
initialised, it enables what Nordic calls a Soft Device. This Soft Device runs 
the Bluetooth stack and also takes over control of some parts of the hardware 
in the process. If other components of the software need access to hardware 
controlled by the Soft Device, then they must make calls to the Soft Device to 
perform the necessary actions on their behalf. The USB driver relies on events 
from the hardware to inform it when it is attached to a host so it knows when 
to enumerate and begin communicating. These hardware events happen to be blocked 
by the Soft Device, so if the USB driver wants to receive them it must arrange 
this with the Soft Device after it has been enabled. The USB initialisation 
functions provided by the Nordic SDK will check if the Soft Device is enabled or 
not and set things up accordingly. The problem we experienced was a result of 
initialising USB first, then Bluetooth, which in turn enables the Soft Device. 
At the time USB was initialised, the Soft Device was not enabled so the SDK did 
not set up the hardware events to work with the Soft Device. Once the Soft Device 
was enabled by the Bluetooth initialisation, the hardware events would no longer 
work for USB. The result was the USB driver not knowing the device had been 
connected to a host, so it would remain idle and never make any attempt to 
enumerate or communicate with the host. While running in debug mode, there just
happened to be enough time for the hardware events to reach the USB driver after 
it was initialised but before Bluetooth was initialised. The solution to the problem
was to simply enable the Soft Device in the USB initialisation code before it
configures the hardware for USB detection. This way, when the SDK checks if the
Soft Device is enabled it will see that it is, and USB will be configured 
accordingly.

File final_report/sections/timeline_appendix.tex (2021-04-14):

\begin{figure}[!htb]
\makebox[\textwidth][r]{
\begin{ganttchart}[]{2020-11-02}{2021-03-20}
    \mygantttitle \\
% Software
    \ganttgroup{Software}{2020-11-02}{2021-02-20} \\
    \ganttbar{Setup Dev. Env.}{2020-11-02}{2020-11-07} \\
    \ganttbar{USB Debugging Interface}{2020-11-08}{2020-12-19} \\
    \ganttbar{SD Card Driver}{2020-11-08}{2021-01-02} \\
    \ganttbar{Sensor Drivers}{2020-11-08}{2021-01-09} \\
    \ganttbar{Filesystem}{2020-12-12}{2021-01-16} \\
    \ganttbar{Bluetooth Interface}{2020-12-19}{2021-01-30} \\
    \ganttbar{Data Logging}{2020-12-26}{2021-01-30} \\
    \ganttbar{Companion Software}{2021-01-02}{2021-02-20} \\

% Testing
    \ganttbar{Sensor Driver Tests}{2021-01-09}{2021-02-13} \\

% Elec
    \ganttgroup{Hardware}{2020-11-02}{2021-03-06} \\
    \ganttbar{Electrical Schematic}{2020-11-02}{2020-12-12} \\
    \ganttbar{PCB Rev. A}{2020-12-13}{2021-01-30} \\
    \ganttbar{PCB Rev. B}{2021-01-31}{2021-03-06} \\

% Mech
    \ganttgroup{Enclosure}{2020-11-02}{2021-03-08} \\
    \ganttbar{Enclosure Prototype A}{2020-11-02}{2020-12-19} \\
    \ganttbar{Enclosure Prototype B}{2021-01-23}{2021-02-03} \\
    \ganttbar{Final Enclosure}{2021-02-27}{2021-03-08} \\
\end{ganttchart}
}
\caption{Original Project Timeline}
\label{fig:original-project-timeline}
\end{figure}

\begin{figure}[!htb]
\makebox[\textwidth][r]{
\begin{ganttchart}[]{2020-11-02}{2021-03-20}
    \mygantttitle \\
% Software
    \ganttgroup{Software}{2020-11-02}{2021-03-08} \\
    \ganttbar{Setup Dev. Env.}{2020-11-02}{2020-12-24} \\
    \ganttbar{USB Debugging Interface}{2020-12-25}{2021-01-22} \\
    \ganttbar{SD Card Driver}{2021-01-15}{2021-02-01} \\
    \ganttbar{Sensor Drivers}{2021-01-15}{2021-02-12} \\
    \ganttbar{Filesystem}{2021-01-22}{2021-02-19} \\
    \ganttbar{Bluetooth Interface}{2021-01-29}{2021-02-26} \\
    \ganttbar{Data Logging}{2021-02-05}{2021-02-19} \\
    \ganttbar{Companion Software}{2021-02-12}{2021-03-08} \\

% Testing
    \ganttbar{Sensor Driver Tests}{2021-02-05}{2021-03-08} \\

% Elec
    \ganttgroup{Hardware}{2020-11-02}{2021-03-06} \\
    \ganttbar{Electrical Schematic}{2020-11-02}{2020-12-24} \\
    \ganttbar{PCB Layout}{2020-12-24}{2020-12-31} \\
    \ganttbar{PCB Assembly}{2021-01-20}{2021-02-10} \\

% Mech
    \ganttgroup{Enclosure}{2021-01-01}{2021-02-26} \\
    \ganttbar{Enclosure Prototype}{2021-01-01}{2021-01-25} \\
    \ganttbar{Final Enclosure}{2021-02-12}{2021-02-26} \\
\end{ganttchart}
}
\caption{Progress Report Timeline}
\label{fig:progress-timeline}
\end{figure}

\begin{figure}[!htb]
\makebox[\textwidth][r]{
\begin{ganttchart}[]{2020-11-02}{2021-03-20}
    \mygantttitle \\
% Software
    \ganttgroup{Software}{2020-11-02}{2021-03-08} \\
    \ganttbar{Setup Dev. Env.}{2020-11-02}{2020-12-24} \\
    \ganttbar{USB Debugging Interface}{2020-12-25}{2021-01-22} \\
    \ganttbar{SD Card Driver}{2021-01-15}{2021-02-01} \\
    \ganttbar{Sensor Drivers}{2021-01-20}{2021-03-05} \\
    \ganttbar{Filesystem}{2021-01-22}{2021-02-19} \\
    \ganttbar{Bluetooth Interface}{2021-01-29}{2021-02-26} \\
    \ganttbar{Data Logging}{2021-02-05}{2021-02-19} \\
    \ganttbar{Companion Software}{2021-02-12}{2021-03-08} \\

% Testing
    \ganttbar{Sensor Driver Tests}{2021-02-05}{2021-03-08} \\

% Elec
    \ganttgroup{Hardware}{2020-11-02}{2021-02-27} \\
    \ganttbar{Electrical Schematic}{2020-11-02}{2020-12-24} \\
    \ganttbar{PCB Layout}{2020-12-24}{2020-12-31} \\
    \ganttbar{PCB Assembly}{2021-01-20}{2021-02-27} \\

% Mech
    \ganttgroup{Enclosure}{2021-02-01}{2021-03-15} \\
    \ganttbar{Enclosure Prototype}{2021-02-01}{2021-02-27} \\
    \ganttbar{Final Enclosure}{2021-03-05}{2021-03-15} \\
\end{ganttchart}
}
\caption{Final Project Timeline}
\label{fig:final-project-timeline}
\end{figure}

\begin{figure}[!htb]
\makebox[\textwidth][r]{
\begin{ganttchart}[]{2020-11-02}{2021-03-20}
    \mygantttitle \\
% Software
    \ganttgroup{Software}{2020-11-02}{2021-03-08} \\
    \ProposalProgressBar{Setup Dev. Env.}{2020-11-02}{2020-11-07}{2020-11-02}{2020-12-24} \\
    \ProposalProgressBar{USB Debugging Interface}{2020-11-08}{2020-12-19}{2020-12-25}{2021-01-22} \\
    \ProposalProgressBar{SD Card Driver}{2020-11-08}{2021-01-02}{2021-01-15}{2021-02-01} \\
    \ProposalProgressBar{Sensor Drivers}{2020-11-08}{2021-01-09}{2021-01-15}{2021-02-12} \\
    \ProposalProgressBar{Filesystem}{2020-12-12}{2021-01-16}{2021-01-22}{2021-02-19} \\
    \ProposalProgressBar{Bluetooth Interface}{2020-12-19}{2021-01-30}{2021-01-29}{2021-02-26} \\
    \ProposalProgressBar{Data Logging}{2020-12-26}{2021-01-30}{2021-02-05}{2021-02-19} \\
    \ProposalProgressBar{Companion Software}{2021-01-02}{2021-02-20}{2021-02-12}{2021-03-08} \\

% Testing
    \ProposalProgressBar{Sensor Driver Tests}{2021-01-09}{2021-02-13}{2021-02-05}{2021-03-08} \\

% Elec
    \ganttgroup{Hardware}{2020-11-02}{2021-03-06} \\
    \ProposalProgressBar{Electrical Schematic}{2020-11-02}{2020-12-12}{2020-11-02}{2020-12-24} \\
    \proposalBar{PCB Rev. A}{2020-12-13}{2021-01-30} \\
    \proposalBar{PCB Rev. B}{2021-01-31}{2021-03-06} \\
    \progressBar{PCB Layout}{2020-12-24}{2020-12-31} \\
    \progressBar{PCB Assembly}{2021-01-20}{2021-02-10} \\

% Mech
    \ganttgroup{Enclosure}{2020-11-02}{2021-03-08} \\
    \ProposalProgressBar{Enclosure Prototype A}{2020-11-02}{2020-12-19}{2021-01-01}{2021-01-25} \\
    \proposalBar{Enclosure Prototype B}{2021-01-23}{2021-02-03} \\
    \ProposalProgressBar{Final Enclosure}{2021-02-27}{2021-03-08}{2021-02-12}{2021-02-26} \\
\end{ganttchart}
}
\begin{itemize}
    \item \colorbox{rgb:\proposalColor,1;white,1}{Proposal Timeline}
    \item \colorbox{rgb:\progressColor,1;white,1}{Progress Timeline}
    \item \colorbox{rgb:\progressColor,2;\proposalColor,1;white,2}{Overlap}
\end{itemize}
\caption{Timeline changes from progress report}
\label{fig:proposal-progress-timeline}
\end{figure}

\begin{figure}[!htb]
\makebox[\textwidth][r]{
\begin{ganttchart}[]{2020-11-02}{2021-03-20}
    \mygantttitle \\
% Software
    \ganttgroup{Software}{2020-11-02}{2021-03-08} \\
    \ProgressFinalBar{Setup Dev. Env.}{2020-11-02}{2020-12-24}{2020-11-02}{2020-12-24} \\
    \ProgressFinalBar{USB Debugging Interface}{2020-12-25}{2021-01-22}{2020-12-25}{2021-01-22} \\
    \ProgressFinalBar{SD Card Driver}{2021-01-15}{2021-02-01}{2021-01-15}{2021-02-01} \\
    \ProgressFinalBar{Sensor Drivers}{2021-01-15}{2021-02-12}{2021-01-20}{2021-03-05} \\
    \ProgressFinalBar{Filesystem}{2021-01-22}{2021-02-19}{2021-01-22}{2021-02-19} \\
    \ProgressFinalBar{Bluetooth Interface}{2021-01-29}{2021-02-26}{2021-01-29}{2021-02-26} \\
    \ProgressFinalBar{Data Logging}{2021-02-05}{2021-02-19}{2021-02-05}{2021-02-19} \\
    \ProgressFinalBar{Companion Software}{2021-02-12}{2021-03-08}{2021-02-12}{2021-03-08} \\

% Testing
    \ProgressFinalBar{Sensor Driver Tests}{2021-02-05}{2021-03-08}{2021-02-05}{2021-03-08} \\

% Elec
    \ganttgroup{Hardware}{2020-11-02}{2021-02-27} \\
    \ProgressFinalBar{Electrical Schematic}{2020-11-02}{2020-12-24}{2020-11-02}{2020-12-24} \\
    \ProgressFinalBar{PCB Layout}{2020-12-24}{2020-12-31}{2020-12-24}{2020-12-31} \\
    \ProgressFinalBar{PCB Assembly}{2021-01-20}{2021-02-10}{2021-01-20}{2021-02-27} \\

% Mech
    \ganttgroup{Enclosure}{2021-02-01}{2021-03-15} \\
    \ProgressFinalBar{Enclosure Prototype}{2021-01-01}{2021-01-25}{2021-02-01}{2021-02-27} \\
    \ProgressFinalBar{Final Enclosure}{2021-02-12}{2021-02-26}{2021-03-05}{2021-03-15} \\
\end{ganttchart}
}
\begin{itemize}
    \item \colorbox{rgb:\finalColor,1;white,1}{Final Timeline}
    \item \colorbox{rgb:\progressColor,1;white,1}{Progress Timeline}
    \item \colorbox{rgb:\progressColor,1;\finalColor,2;white,2}{Overlap}
\end{itemize}
\caption{Final timeline changes from progress report}
\label{fig:progress-final-timeline}
\end{figure}

\begin{figure}[!htb]
\makebox[\textwidth][r]{
\begin{ganttchart}[]{2020-11-02}{2021-03-20}
    \mygantttitle \\
% Software
    \ganttgroup{Software}{2020-11-02}{2021-03-08} \\
    \ProposalFinalBar{Setup Dev. Env.}{2020-11-02}{2020-11-07}{2020-11-02}{2020-12-24} \\
    \ProposalFinalBar{USB Debugging Interface}{2020-11-08}{2020-12-19}{2020-12-25}{2021-01-22} \\
    \ProposalFinalBar{SD Card Driver}{2020-11-08}{2021-01-02}{2021-01-15}{2021-02-01} \\
    \ProposalFinalBar{Sensor Drivers}{2020-11-08}{2021-01-09}{2021-01-20}{2021-03-05} \\
    \ProposalFinalBar{Filesystem}{2020-12-12}{2021-01-16}{2021-01-22}{2021-02-19} \\
    \ProposalFinalBar{Bluetooth Interface}{2020-12-19}{2021-01-30}{2021-01-29}{2021-02-26} \\
    \ProposalFinalBar{Data Logging}{2020-12-26}{2021-01-30}{2021-02-05}{2021-02-19} \\
    \ProposalFinalBar{Companion Software}{2021-01-02}{2021-02-20}{2021-02-12}{2021-03-08} \\

% Testing
    \ProposalFinalBar{Sensor Driver Tests}{2021-01-09}{2021-02-13}{2021-02-05}{2021-03-08} \\

% Elec
    \ganttgroup{Hardware}{2020-11-02}{2021-03-06} \\
    \ProposalFinalBar{Electrical Schematic}{2020-11-02}{2020-12-12}{2020-11-02}{2020-12-24} \\
    \proposalBar{PCB Rev. A}{2020-12-13}{2021-01-30} \\
    \proposalBar{PCB Rev. B}{2021-01-31}{2021-03-06} \\
    \finalBar{PCB Layout}{2020-12-24}{2020-12-31} \\
    \finalBar{PCB Assembly}{2021-01-20}{2021-02-27} \\

% Mech
    \ganttgroup{Enclosure}{2021-02-01}{2021-03-15} \\
    \ProposalFinalBar{Enclosure Prototype}{2020-11-02}{2020-12-19}{2021-02-01}{2021-02-27} \\
    \proposalBar{Enclosure Prototype B}{2021-01-23}{2021-02-03} \\
    \ProposalFinalBar{Final Enclosure}{2021-02-27}{2021-03-08}{2021-03-05}{2021-03-15} \\
\end{ganttchart}
}
\begin{itemize}
    \item \colorbox{rgb:\finalColor,1;white,1}{Final Timeline}
    \item \colorbox{rgb:\proposalColor,1;white,1}{Proposal Timeline}
    \item \colorbox{rgb:\proposalColor,1;\finalColor,2;white,2}{Overlap}
\end{itemize}
\caption{Final timeline changes from proposal}
\label{fig:proposal-final-timeline-appendix}
\end{figure}

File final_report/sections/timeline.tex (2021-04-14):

We created an initial timeline for our proposal which was revised for the
progress report.  Then finally we created a final timeline that reflects what
has actually occurred.  All three timelines are available in appendix
section \ref{sec:appendix-timelines}.

Our original timeline was very optimistic and ending up changing quite
dramatically.  Figure \ref{fig:proposal-final-timeline} shows the changes that
occurred.

Software development was started much later than intended. There are a few
explanations for this.  The software development environment was more difficult
to set up than expected as discussed in section \ref{sec:toolchain-issues}.
Furthermore, there was a discouraging lack of feedback since there was no
hardware to test on.

The most prominent change in hardware is the elimination of a second PCB
revision. Thankfully, only having one revision did not prevent us from making a
functional product, but this eliminate was done to save time, not because we
had a flawless first PCB revision.

The enclosure was delayed due to hardware assembly and part availability
issues.  The idea behind the enclosure design was to rapidly iterate the case
with the PCB in hand.  However, assembly and part availability issues meant the
hand off of the PCB to the case designer happened much later than expected.

\ganttset{
    calendar week text={\currentweek},
    y unit title=0.5cm, y unit chart=0.5cm,
    vgrid,
    x unit = 1mm,
    time slot format=isodate,
    time slot unit=day,
    title/.append style={draw=none, fill=RoyalBlue!50!black},
    title label font=\sffamily\scriptsize\color{white},
    title label node/.append style={below=-1.6ex},
    title left shift=.05,
    title right shift=-.05,
    title height=1,
    bar height=.6,
    group right shift=0,
    group top shift=.6,
    group height=.3,
    group peaks height=.2,
    bar incomplete/.append style={fill=Maroon},
    bar label node/.style={text width=3cm,align=right,font=\scriptsize\RaggedLeft,anchor=east},
    milestone label node/.style={text width=2cm,align=right,font=\scriptsize\RaggedLeft,anchor=east},
    group label node/.style={text width=3cm,align=right,font=\textbf\scriptsize\RaggedLeft,anchor=east},
    bar/.append style={opacity=0.5}
}

\newcommand\mygantttitle {
    \gantttitlecalendar{year} \\
    \gantttitlecalendar{month} \\
    \gantttitlecalendar{week}
}

\newcommand\proposalColor{blue!70}
\newcommand\progressColor{red!70}
\newcommand\finalColor{green!70}

\newcommand\proposalBar[3]
{\ganttbar[bar/.append style={fill=\proposalColor}]{#1}{#2}{#3}}
\newcommand\progressBar[3]
{\ganttbar[bar/.append style={fill=\progressColor}]{#1}{#2}{#3}}
\newcommand\finalBar[3]
{\ganttbar[bar/.append style={fill=\finalColor}]{#1}{#2}{#3}}

\newcommand\ProposalProgressBar[5]
{\proposalBar{#1}{#2}{#3}\progressBar{}{#4}{#5}}

\newcommand\ProgressFinalBar[5]
{\progressBar{#1}{#2}{#3}\finalBar{}{#4}{#5}}

\newcommand\ProposalFinalBar[5]
{\proposalBar{#1}{#2}{#3}\finalBar{}{#4}{#5}}

\begin{figure}[!htb]
\makebox[\textwidth][r]{
\begin{ganttchart}[]{2020-11-02}{2021-03-20}
    \mygantttitle \\
% Software
    \ganttgroup{Software}{2020-11-02}{2021-03-08} \\
    \ProposalFinalBar{Setup Dev. Env.}{2020-11-02}{2020-11-07}{2020-11-02}{2020-12-24} \\
    \ProposalFinalBar{USB Debugging Interface}{2020-11-08}{2020-12-19}{2020-12-25}{2021-01-22} \\
    \ProposalFinalBar{SD Card Driver}{2020-11-08}{2021-01-02}{2021-01-15}{2021-02-01} \\
    \ProposalFinalBar{Sensor Drivers}{2020-11-08}{2021-01-09}{2021-01-20}{2021-03-05} \\
    \ProposalFinalBar{Filesystem}{2020-12-12}{2021-01-16}{2021-01-22}{2021-02-19} \\
    \ProposalFinalBar{Bluetooth Interface}{2020-12-19}{2021-01-30}{2021-01-29}{2021-02-26} \\
    \ProposalFinalBar{Data Logging}{2020-12-26}{2021-01-30}{2021-02-05}{2021-02-19} \\
    \ProposalFinalBar{Companion Software}{2021-01-02}{2021-02-20}{2021-02-12}{2021-03-08} \\

% Testing
    \ProposalFinalBar{Sensor Driver Tests}{2021-01-09}{2021-02-13}{2021-02-05}{2021-03-08} \\

% Elec
    \ganttgroup{Hardware}{2020-11-02}{2021-03-06} \\
    \ProposalFinalBar{Electrical Schematic}{2020-11-02}{2020-12-12}{2020-11-02}{2020-12-24} \\
    \proposalBar{PCB Rev. A}{2020-12-13}{2021-01-30} \\
    \proposalBar{PCB Rev. B}{2021-01-31}{2021-03-06} \\
    \finalBar{PCB Layout}{2020-12-24}{2020-12-31} \\
    \finalBar{PCB Assembly}{2021-01-20}{2021-02-27} \\

% Mech
    \ganttgroup{Enclosure}{2021-02-01}{2021-03-15} \\
    \ProposalFinalBar{Enclosure Prototype}{2020-11-02}{2020-12-19}{2021-02-01}{2021-02-27} \\
    \proposalBar{Enclosure Prototype B}{2021-01-23}{2021-02-03} \\
    \ProposalFinalBar{Final Enclosure}{2021-02-27}{2021-03-08}{2021-03-05}{2021-03-15} \\
\end{ganttchart}
}
\begin{itemize}
    \item \colorbox{rgb:\finalColor,1;white,1}{Final Timeline}
    \item \colorbox{rgb:\proposalColor,1;white,1}{Proposal Timeline}
    \item \colorbox{rgb:\proposalColor,1;\finalColor,2;white,2}{Overlap}
\end{itemize}
\caption{Final timeline changes from proposal}
\label{fig:proposal-final-timeline}
\end{figure}

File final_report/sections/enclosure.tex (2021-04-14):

The enclosure was difficult to construct for multiple reasons.  In order to
minimize the size of the PCB, we decided to forgo traditional mounting holes.
Additionally, we avoided using adhesive to mount the PCB in order to maintain
easy access for debugging and repair purposes.  This means the enclosure needed
tight tolerances around the PCB to prevent horizontal and vertical movement.
Additionally, the sensors mounted on the bottom of the PCB need to be a precise
distance away from the users wrist.  This means the thickness of the bottom of
the enclosure needed to be accurately tuned.

To add difficulty to the situation, the enclosure was manufactured by a (rather
cheap) desktop FDM 3D printer.  These printers are known for over extruding
plastic which causes the produced part to be slightly larger in the X and Y
dimensions.  As over extruding is preferable to under extruding (which weakens
the structural integrity of the part), it is common to simply model the part
slightly smaller to compensate.

FDM printers also tend to warp parts if the plastic cools too quickly, but that
can be countered by simply putting the printer in a warm room or giving the
printer a cozy blanket (although that is a fire hazard).

However, FDM 3D printing is exceptionally fast.  They make it possible to
iterate and print a 3D model of this size multiple times per day.  This rapid
iteration has enabled us to create parts that meet the above requirements.

The need for rapid iteration has led to the creation of many parametric 3D
modeling programs.  The idea is to define variables (like the the thickness of
the bottom of the model) that can easily be changed.  The problem with many of
these modeling programs is that they simply save a series of steps the user has
entered with the GUI so they can later replay this with different values.  This
replay of events is very error prone and usually requires a lot of human
intervention.  This is because the interface makes it difficult to specify
geometry that is valid for a wide parameter range.

For this reason, OpenSCAD was used.  OpenSCAD defines 3D models in its
scripting language which is executed to produce 3D printable files.  Since
every usage of a parameter is written out explicitly, it is easy to determine
all the valid values for the parameters.

In the end, 7 iterations where needed to achieve the final enclosure. The 3D
render of the result can bee seen in Figure \ref{fig:enclosure} and the final
fabricated enclosure can be seen in Figure \ref{fig:enclosure-fab}.  Although
the board is held in place solely using friction, it is secure enough to stay in
place even during a rigorous jog while wearing the device.

\begin{figure}[!htb]
\centering
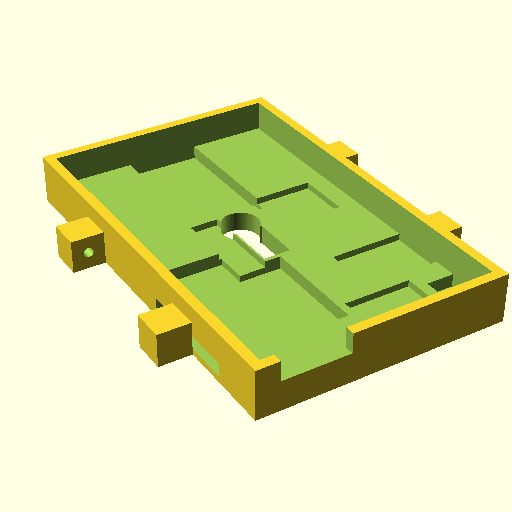
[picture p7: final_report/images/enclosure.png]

\caption{Enclosure Render}
\label{fig:enclosure}
\end{figure}

\begin{figure}[!htb]
\centering
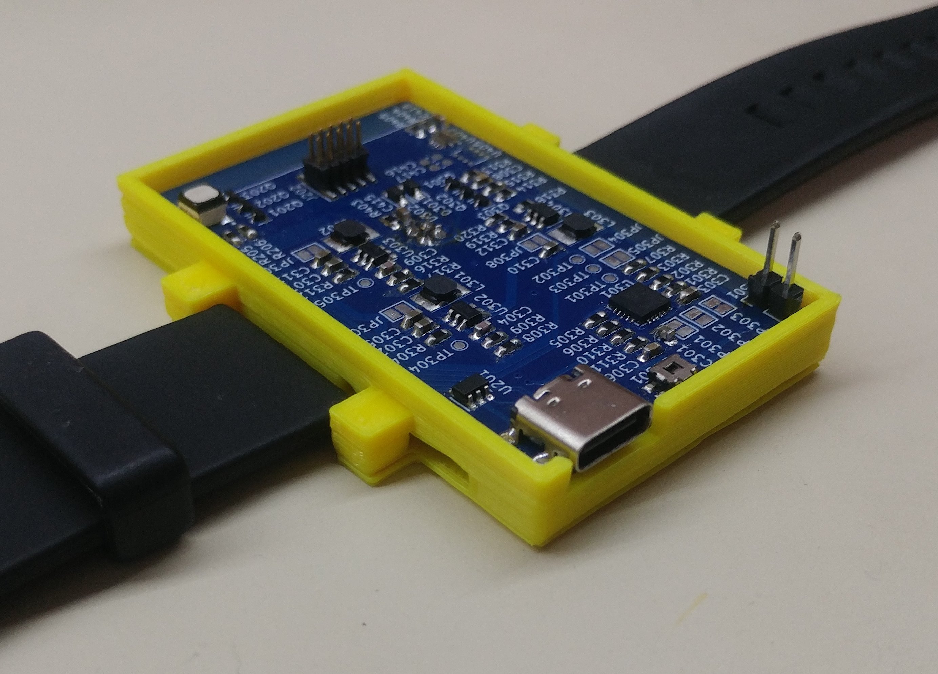
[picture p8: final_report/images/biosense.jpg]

\caption{Fabricated Enclosure with watch straps and a board installed}
\label{fig:enclosure-fab}
\end{figure}

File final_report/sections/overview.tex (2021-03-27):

This section provides an overview of the problem this project aims to solve,
why it is important, how this project can be part of the solution, and finally
a brief description of what was accomplished. Subsequent sections of this
report cover the hardware and software design of the project in detail, as well
as discuss some of the challenges that were faced in pursuing the solution
outlined here. Information regarding the tests performed on the final project
are also detailed in this report, and a series of appendices are included with
visuals to show some interesting parts of the design and what the final product
looks like.

\subsection{Background}

Traditionally, people only seek treatment for ailments after they start
experiencing symptoms; however, it is often desirable to take action before
symptoms appear.  One solution to catch illness earlier could be to monitor a
person's physiological state using various sensors and take action when the
state falls outside of a known healthy state.  However, the accepted healthy
range for a population could be significantly larger than the accepted healthy
range for the individual \cite{Wearable-tracking2017}.

Wearables are capable of revealing personal daily physiological cycles with
respect to skin temperature, and heart rate with high accuracy
\cite{Wearable-tracking2017}. By comparing a person's current physiological
state with the expected state, it is possible to predict illness with greater
sensitivity than a self diagnosis. For example, a study was able to detect a
period of inflammation (confirmed by a medical high-sensitivity C-reactive
protein test) using a participant's heart rate even though the participant
themselves experienced no symptoms \cite{Wearable-tracking2017}.  The same
study even helped a participant get treatment of Lyme disease before the
``Bull's eye'' rash appeared (a common symptom during the early stages of Lyme
disease) by detecting an abnormality in their SpO\textsubscript{2} levels.

Wearable data can also be used to detect group illness rates.  By using heart
rate data and sleep data from fitbit devices and cross referencing that data
with the Centers for Disease Control and Prevention's (CDC) Influenza Like
Illness (ILI) data, a study was able to predict illness 6.3\% to 32.9\% better
than previous methods \cite{Radin2020}.

Wearables can also detect more immediate dangers to someone's health like a
heart attack \cite{heart-attack}, a fall \cite{Khojasteh_2018}, or dangerously
low or high heart rates.  This information could be used to alert emergency
services to save lives.

\subsection{Motivation}

Despite all of the advances in medical technology, a cure for diseases and
allowing humans to live longer are ever present goals for scientists and 
doctors alike.  Often wide spread diseases we have not prepared for can occur in
society.  COVID-19 is a pandemic that
has, at the time of writing, claimed an estimated 2.5 million lives globally
\cite{johns-hopkins-corona-chan}, and continues to infect more people every
day.  In 2007 it was estimated that the total cost of occupational illnesses
among civilians in the United States was \$58 billion \cite{Leigh2011}.
Slowing the spread of disease could save lives and save money.

One method of limiting the spread of disease is early diagnosis.  This would
allow individuals who are aware they are ill to take measures to reduce the
spread of their illness, even before symptoms manifest.  This will be
particularly useful for healthcare providers who work with high risk
individuals, since identifying symptoms early has the highest efficiency for
protecting others.

By creating a personal physiological profile and constantly
comparing the user's current physiological state to it, illness can be detected
early.  The motivation for our project is to create a device capable of measuring 
enough of the user's current physiological state to predict illness.  This is done 
in the hope that it could be used to slow the spread of illness's and, to speed
recovery from illness's by starting treatment earlier.

\subsection{Problem Statement}

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

\subsection{Solution}

The solution provided by this project is a wrist mounted wearable health 
monitoring device. The device provides a sensor platform that is suitable for 
early detection of disease. The included sensors can measure skin temperature, 
ambient temperature, heart rate, pulse oximetry, and motion.  The electronic
components fit into a comfortable, wearable 3D printed plastic enclosure.
The device is powered by a lithium polymer battery which can be recharged
through the USB-C connector.
% \todo{missing UV light sensor?}

The wearable device has limited user interfaces consisting of an indicator
LED for power, notifications, and debugging. It also features a power button
to turn the device on and off. The main interactions with the device occur 
through a companion software that connects to the device through Bluetooth or 
USB. It is limited to simply receiving and decoding data received from the 
wearable device, and exporting it in an analyzable format such as a csv or json 
file.

The device will store the collected sensor information to a micro SD card
in the device which is then read back when requested via the companion software.
The SD card will be replaceable, and the capacity of the card used will dictate
how long the device can record data before needing to off load to the companion
software.

The focus of this solution is on the collection of biometrics and making them
available for analysis. No attempt was made to perform medical analysis
or give clinical diagnosis from the collected biometrics. Our intention was to
design the system so that those applications could be integrated with or built
on top of the work we have done for this project.

%Should this be in a reflection or something? Not really part of a solution,
%it is a disclaimer.

%In order to reduce development cost and complexity, the hardware component of
%the project uses sensors that are readily available from online sources, and 
%that can be assembled on a PCB by hand relatively easily. As a result the 
%selection of sensors may be more limited or lower quality than what is possible 
%if options that are made to order, or only available in large quantities had been
%explored.  The use of parts that can be soldered to a PCB without paying for
%the services of an advanced manufacturing facility also resulted in the final 
%hardware design being larger than it would have been otherwise.

\subsection{Accomplishments}

Our team successfully created a wrist mounted wearable health monitoring device
that is capable of measuring skin temperature, ambient temperature, heart rate,
pulse oximetry, and motion..  The hardware is fully functional and correctly
connects all the selected components together.  The software is able to connect
the device to companion software located on a separate device using Bluetooth
and USB.  We are able to log motion and temperature sensor to the SD Card.

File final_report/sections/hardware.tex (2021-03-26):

This section will describe the hardware component of the project and explain 
the rationale for some important design decisions including component selection,
schematic design, and component placement on the PCB. It will also detail any 
variations from what was planned in the project proposal and why these changes
were made.

\subsection{Component Selection}

We considered a number of requirements in choosing a microcontroller for our
project. We identified several microcontroller features that were needed to
support our project requirements and did not consider any microcontrollers
without these features. These features are:
\begin{itemize}
    \item Bluetooth Low Energy support
    \item At least one I2C master mode interface for sensors
    \item An SPI or SD/MMC interface to connect and SD card
\end{itemize}

While we could have selected from a much wider variety of microcontrollers if we
had considered using a separate Bluetooth LE controller chip, we chose to limit
our selection to parts that featured an integrated Bluetooth LE radio. This is
to reduce part count (and therefore size, cost and design complexity) and to
provide better power consumption.

Table \ref{tab:mcu-comp-general} shows a brief summary of the microcontroller
options that we considered, all of which meet the minimum criteria outlined
above. The costs listed in the table are the price in Canadian dollars in single
quantities in the friendliest device package available and cut tape or tray
packaging from digikey.ca. These prices are often volatile and are therefore
listed here only for relative comparison.

All of the parts listed are based on ARM cortex processors. Nordic
Semiconductor's nRF5340 and the Silicon Labs EFR32BG22C224 use a Cortex-M33
while all of the other microcontrollers listed use a Cortex-M4. We estimated that
any of these microcontrollers would have sufficient processor performance for
our application. Similarly, all of the listed options have ample flash storage
and SRAM.

Not all of the listed microcontrollers come in packages that are easy to solder
by hand. The relatively small QFN packages of the nRF52832 and EFR32BG22C224 can
be soldered with relative ease using a hot air reflow station or an iron and be
inspected easily with a microscope. Unfortunately the other options are much
more difficult, the Apollo3 Blue's BGA package and the WLP package of the
MAX32668 each have a large array of solder balls. These packages can be soldered
with hot air reflow, but we did not have the equipment to inspect them. The
nRF52840 and nRF5340 are a middle ground, their aQFN packages have many fewer
balls, but they still do have two rows of connections. This means that while we
are able to solder the packages with hot air reflow they would difficult to
inspect. Another option that was considered to sidestep the issue of soldering 
difficulty entirely was the use of modules that integrate the microcontroller and
a PCB antenna on a small PCB. The nRF52840 and nRF52830 can be found in these
modules and the Apollo3 Blue is available in a similar module from SparkFun
branded as SparkFun Artemis.

The availability was also a limiting factor in our decision. Most of our listed
microcontrollers were readily available from a variety of online component
vendors. The exception was the Apollo3 Blue, which was not readily available
outside of SparkFun's Artemis module, and the MAX32668 which is a newly
available part and could only be ordered as a sample from Maxim's
website.

\begin{table*}[!htb]
\centering
\begin{tabular}{>{\centering\arraybackslash}m{2.2cm}|
                >{\centering\arraybackslash}m{2.5cm}|
                >{\centering\arraybackslash}m{2.0cm}|
                >{\centering\arraybackslash}m{1.5cm}|
                >{\centering\arraybackslash}m{1.2cm}|
                >{\centering\arraybackslash}m{1.8cm}|
                >{\centering\arraybackslash}m{1.2cm}}
\toprule
Part Number & Manufacturer & CPU & Program Memory & SRAM & Friendliest Package & Cost \\
\midrule
\textbf{nRF52840} & \textbf{Nordic Semiconductor} & \textbf{ARM Cortex-M4 at 64 MHz} & \textbf{1 MiB} & \textbf{256 KiB}  & \textbf{aQFN73} & \textbf{\$9.34} \\
nRF52832 & Nordic Semiconductor & ARM Cortex-M4 at 64 MHz & 512 KiB & 64 KiB  & QFN48 & \$8.19 \\
nRF5340 & Nordic Semiconductor & Dual ARM Cortex-M33 at 96/64 MHz & 1 MiB & 512 KiB & aQFN94 & \$13.85 \\
Apollo3 Blue & Ambiq & ARM Cortex-M4 at 48 MHz & 1 MiB & 384 KiB & BGA81 & N/A \\
MAX32668 & Maxim Integrated & ARM Cortex-M4 at 96 MHz & 1 MiB & 560 KiB & WLP109 & N/A \\
EFR32BG22 C224 & Silicon Labs & ARM Cortex-M33 at 76.8 MHz & 512 KiB & 32 KiB & QFN40 & \$5.26 \\
\bottomrule
\end{tabular}
\caption{Comparison of Microcontrollers With Bluetooth Low Energy Radios}
\label{tab:mcu-comp-general}
\end{table*}

Table \ref{tab:mcu-comp-comm} compares the communications interfaces available
on the microcontrollers we considered. All of the microcontrollers feature at
least Bluetooth Low Energy 5.0, at least two I2C interfaces and at least two SPI
interfaces. In addition to these interfaces the MAX32668 has an SD/MMC interface
controller which supports the SD3.0 specification. This interface would allow
significantly faster SD card access speeds than we can accomplish using an SPI
interface.

The nRF52840 and MAX32688 both feature USB interfaces. We decided to have a USB
CDC-ACM interface for debugging and as a wired alternative to the
Bluetooth interface for data transfer. While we could have implemented a USB
interface with any of the microcontrollers listed by using a separate USB to
UART chip, using one of the microcontrollers with a built-in USB interface 
gives us greater integration saving us cost, board space, complexity and
power usage.

\begin{table*}[!htb]
\centering
\begin{tabular}{>{\centering\arraybackslash}m{3.0cm}|
                >{\centering\arraybackslash}m{1.8cm}|
                >{\centering\arraybackslash}m{1.8cm}|
                >{\centering\arraybackslash}m{1.8cm}|
                >{\centering\arraybackslash}m{1.5cm}|
                >{\centering\arraybackslash}m{3.0cm}}
\toprule
Part Number & I2C Master Interfaces & SPI Master Interfaces & SD/MMC Interface & BLE Version & USB \\
\midrule
\textbf{nRF52840} & \textbf{2} & \textbf{4} & \textbf{None} & \textbf{5.2}  & \textbf{2.0 Full Speed} \\
nRF52832 & 2 & 3 & None & 5.2  & None \\
nRF5340 & 4 & 5 & None & 5.1 & None \\
Apollo3 Blue & 6 & 6 & None & 5.0 & None \\
MAX32668 & 3 & 3 & SD3.0 & 5.0 & 2.0 High Speed \\
EFR32BG22C224 & 2 & 2 & None & 5.2 & None \\
\bottomrule
\end{tabular}
\caption{Comparison of Microcontroller Communications Hardware}
\label{tab:mcu-comp-comm}
\end{table*}

While our project did not necessarily require hardware accelerated cryptography,
we thought it should be included to accommodate any future software layers that
build on top of our platform. Since the device collects information about the
user it is likely that cryptography would be heavily used by security features,
and software implementations of the cryptographic algorithms may not be adequate.
Table \ref{tab:mcu-comp-crypto} shows the cryptography features of the
microcontrollers that we considered. All of the microcontrollers have suitable
hardware accelerated cryptography features with the exception of the nRF52832
which lacks any modular arithmetic acceleration for public key cryptography and
the Apollo3 Blue which has no hardware cryptography accelerator.

\begin{table*}[!hb]
\centering
\begin{tabular}{>{\centering\arraybackslash}m{2.5cm}|
                >{\centering\arraybackslash}m{2.0cm}|
                >{\centering\arraybackslash}m{2.0cm}|
                >{\centering\arraybackslash}m{2.5cm}|
                >{\centering\arraybackslash}m{2.5cm}|
                >{\centering\arraybackslash}m{1.5cm}}
\toprule
Part Number & Hashes & Public Key Algorithms & Symmetric Key Algorithms & AES Modes & True Random Number Generator \\
\midrule
\textbf{nRF52840} & \textbf{SHA-1, SHA-2 up to 256 bits, HMAC} & \textbf{RSA up to 2048 bit key, ECC} & \textbf{AES128, ChaCha20, Poly1305} & \textbf{ECB, CBC, CMAC/CBC-MAC, CTR, CCM/CCM*} & \textbf{Yes} \\
nRF52832 & None & None & AES128 & ECB, CCM & No \\
nRF5340 & SHA-1, SHA-1 up to 256 bits, HMAC & RSA up to 3072 bit key, ECC & AES128, AES256 & ECB, CBC, CMAC/CBC-MAC, CTR, CCM/CCM*, GCM & Yes \\
Apollo3 Blue & None & None & None & None & No \\
MAX32668 & SHA-2 up to 512 bits & RSA up to 4096 bit key, ECC & AES128, AES192, AES256, DES, 3DES & ECB, CBC, CFB, OFB, CTR & Yes \\
EFR32BG22 C224 & SHA-1, SHA-2 up to 256 bits & ECC & AES128, AES192, AES256 & ECB, CTR, CBC, CFB, GCM, CBC-MAC, GMAC, CCM & Yes \\
\bottomrule
\end{tabular}
\caption{Comparison of Microcontroller Cryptography Hardware}
\label{tab:mcu-comp-crypto}
\end{table*}

Because of its availability, relatively easy to work with package, suitable
serial interface, integrated USB support and hardware cryptography acceleration
we chose to use the nRF52840 microcontroller. The Apollo3 Blue had tempting low 
power features, but questionable availability and a complete lack of hardware 
accelerated cryptography. The MAX32668 would also have been a very strong 
option, but it is not yet widely available. The EFR32BG33C224's lack of an 
integrated USB interface and comparatively little documentation caused us to
choose the nRF52840 over it.

More specifically, it was decided to use a module (BMD-340) containing the
nRF52840 instead of the bare chip itself. This decision was made because 
the module is much more available for purchase, it has a built in Bluetooth 
antenna which has already been certified by several different parties, it is 
easier to solder, and it includes several supporting components for the 
microcontroller such as oscillators and capacitors. The module is more 
expensive and larger than the microcontroller by itself, however when taking 
into consideration the size and cost of the additional components it contains, 
it likely as good or better than using individual components.

The selection of sensors that made it into the final design are an inertial 
measurement unit (IMU), a heart rate sensor, an air quality sensor, a UV light 
sensor, an infrared temperature sensor and an ambient temperature sensor. This 
suite of sensors was selected in order to capture as much information as 
possible without increasing the cost of the device too much. The component 
choice for each of these sensors was mostly driven by cost, availability, and 
ease of soldering. Taking these factors into consideration narrowed down the 
options very quickly. The infrared temperature sensor and ambient temperature 
sensor are both integrated into the same component. The ambient temperature 
sensor will indicate the temperature of the user’s environment while the 
infrared temperature sensor measures the user’s body temperature. The air 
quality sensor and UV light sensor will provide additional information about 
the user’s environment. The IMU will provide information about the user’s 
movements, and the heart rate sensor will measure the user’s heart rate. A
summary of the exact part numbers selected for each type of component discussed 
in this section is provided in Table \ref{tab:component-summary}.

\begin{table*}[!htb]
\centering
\begin{tabular}{>{\centering\arraybackslash}m{7.0cm}|
                >{\centering\arraybackslash}m{3.5cm}|
                >{\centering\arraybackslash}m{3.5cm}}
\toprule
Component & Manufacturer & Part Number \\
\midrule
Prossor module (with nRF52840) & U-Blox & BMD-340 \\
Inertial Measurement Unit (IMU) & TDK & ICM-20948 \\
Heart rate sensor & Maxim Integrated & MAX86150EFF \\
Infrared \& ambient temperature sensor & Amphenol & ZTP-148SR \\
Air quality sensor & Bosch Sensortec & BME680 \\
UV light sensor & Silicon Labs & SI1133-AA00-GM \\
\bottomrule
\end{tabular}
\caption{Summary of component choices}
\label{tab:component-summary}
\end{table*}

\subsection{Schematic}

The schematic is split into three major sections. These are the power supply, 
processor, and sensors. The power supply is responsible for managing the 
devices internal lithium-ion polymer (LiPo) battery and powering all other 
parts of the circuit. When the device has its USB-C port connected to a 
suitable host, the power supply will shift the electrical load from the 
internal battery to the USB power source and begin charging the internal 
battery. When USB power is lost charging stops and the electrical load is 
shifted back to the internal battery. Transitions between the two power 
sources are seamless and will not interrupt operation of the rest of the 
device. Upon request by the processor, the power supply can also perform fast 
charging of the battery. The processor is responsible for communicating with 
all onboard sensors and the internal SD card through several I2C and SPI 
buses. Communication with the outside world is also handled by the processor
through the USB-C port or wirelessly over Bluetooth. The collection of onboard 
sensors is responsible for gathering information about the user and their 
environment to be used by the processor.

The implementation of the power supply was mostly guided by the requirements of 
the rest of the system and cost. The majority of the components in the design 
require 1.8V to operate with the exceptions being the RGB status LED and the SD 
card requiring 3.3V. The status LED does not have a specific voltage 
requirement, but 1.8V was not sufficient to overcome the forward voltage of the 
diodes so 3.3V was used instead with appropriate series current limiting 
resistors. The choice of a LiPo battery meant that the power supply input 
voltage could be anywhere from 3.7V to 2.8V depending on state of charge, and 
when connected to USB power the input would be 5V. There were several ideas on 
how to build a power supply that would meet all the requirements, but the final 
decision is pictured in Figure \ref{fig:BlockDiagram_PowerSupply} as a block 
diagram.

\begin{figure}[!htb]
\centering
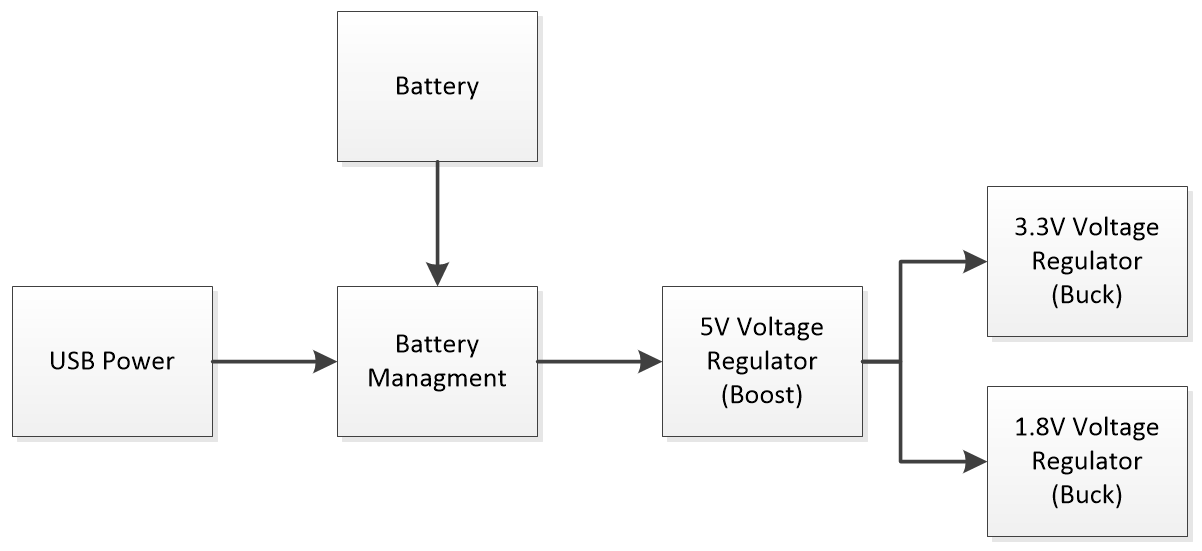
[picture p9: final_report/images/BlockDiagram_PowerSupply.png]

\caption{Block diagram of power supply.}
\label{fig:BlockDiagram_PowerSupply}
\end{figure}

The battery and USB power input are both connected directly to a dedicated 
battery management IC. This IC handles battery charging, battery protection, 
and automatic switchover from one power source to the other. It does not 
however provide any means of regulation. Regulation is handled by three 
separate voltage regulators, the first of which boosts the input up to 5V. The 
last two regulators step the output of the 5V regulator down to 3.3V and 1.8V. 
The intermediate 5V is not strictly necessary as 5V is not used anywhere in the 
design, but without it the 3.3V regulator would need to be a more expensive 
buck-boost type since the input voltage could be above or below its output. 
Additionally, the 5V regulator has an enable input that is used in conjunction 
with some soft power on/off circuitry to completely isolate the load from the 
power source and reduce standby power consumption to nearly zero. Another option 
that was considered was using the voltage regulator built into the chosen 
processor to generate the 1.8V from 3.3V. It was ultimately decided not to go 
this route due to concerns over robustness and maximum current limitations. With 
the current design, both the 3.3V and 1.8V regulators can operate independent of 
each other, have short circuit protection with automatic recovery, have over 
temperature protection, can deliver much more current than needed, and should 
operate with over 90\% efficiency according to the device datasheets. The result 
is a very robust, safe, and cheap solution that integrates well with the rest of 
the design.
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

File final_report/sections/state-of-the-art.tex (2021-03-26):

Wearable health monitoring devices have been progressing in areas including
form factor, biometric data collection, and battery life.  This section will
discuss the current state of commercially available solutions, as well as some
ongoing research areas.

Commercially available wearable health monitoring devices come in a variety of
different form factors depending on their intended use and their capabilities.
These include wrist-mounted devices such as smartwatches and wrist bands,
head-mounted devices, straps, textiles, and various
others \cite{Seneviratne2017}.  The type of device most relevant to this
proposal is the wrist band.  They may be equipped with a selection of sensors
and a processor, but have no display.  An example of such a device shown in 
Figure \ref{fig:EmpaticaE4} is the Empatica E4 wristband \cite{McCarthy2016}.  
This device is designed to provide real-time
physiological data for research using a photoplethysmogram, electrodermal
activity sensor, accelerometer, and temperature sensor \cite{empatica}. The
device can log data internally, stream it over Bluetooth, and has an API for
developing smartphone apps that make use of the data it collects. Empatica
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

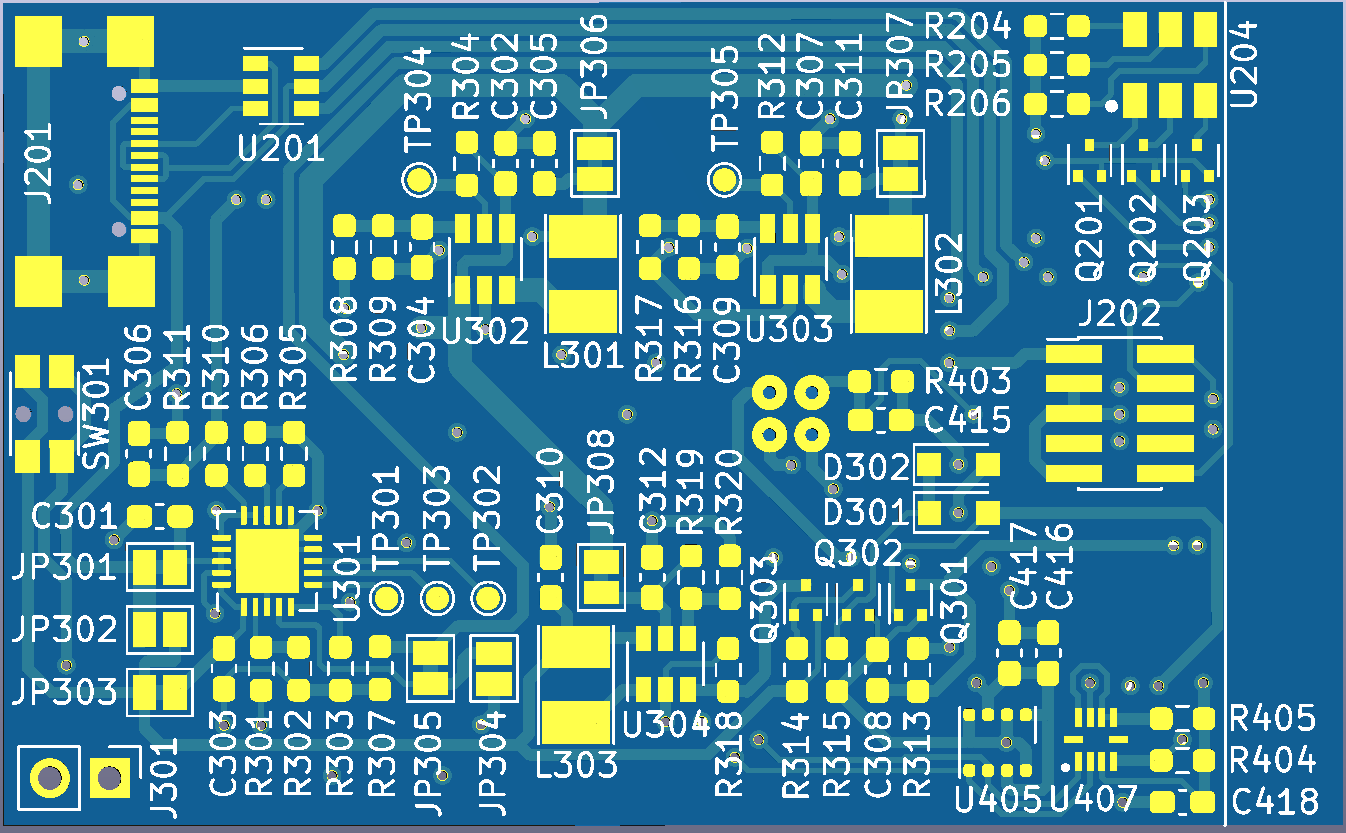
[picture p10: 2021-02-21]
final_report/images/Board_Top.png

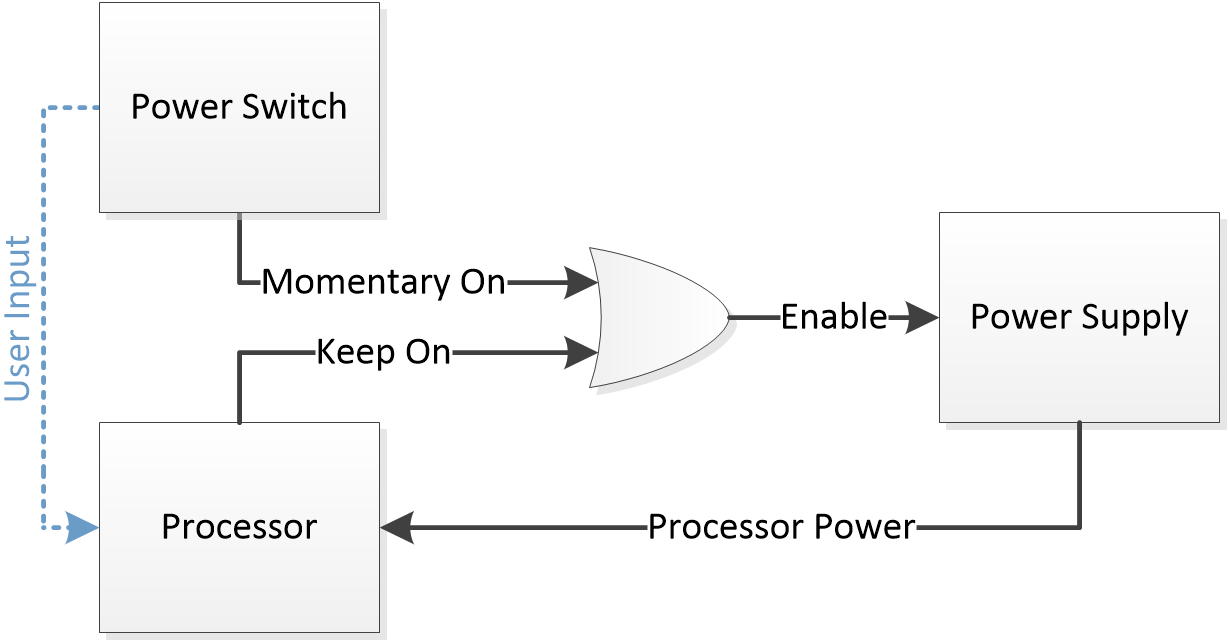
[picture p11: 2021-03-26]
final_report/images/BlockDiagram_OnOff.png

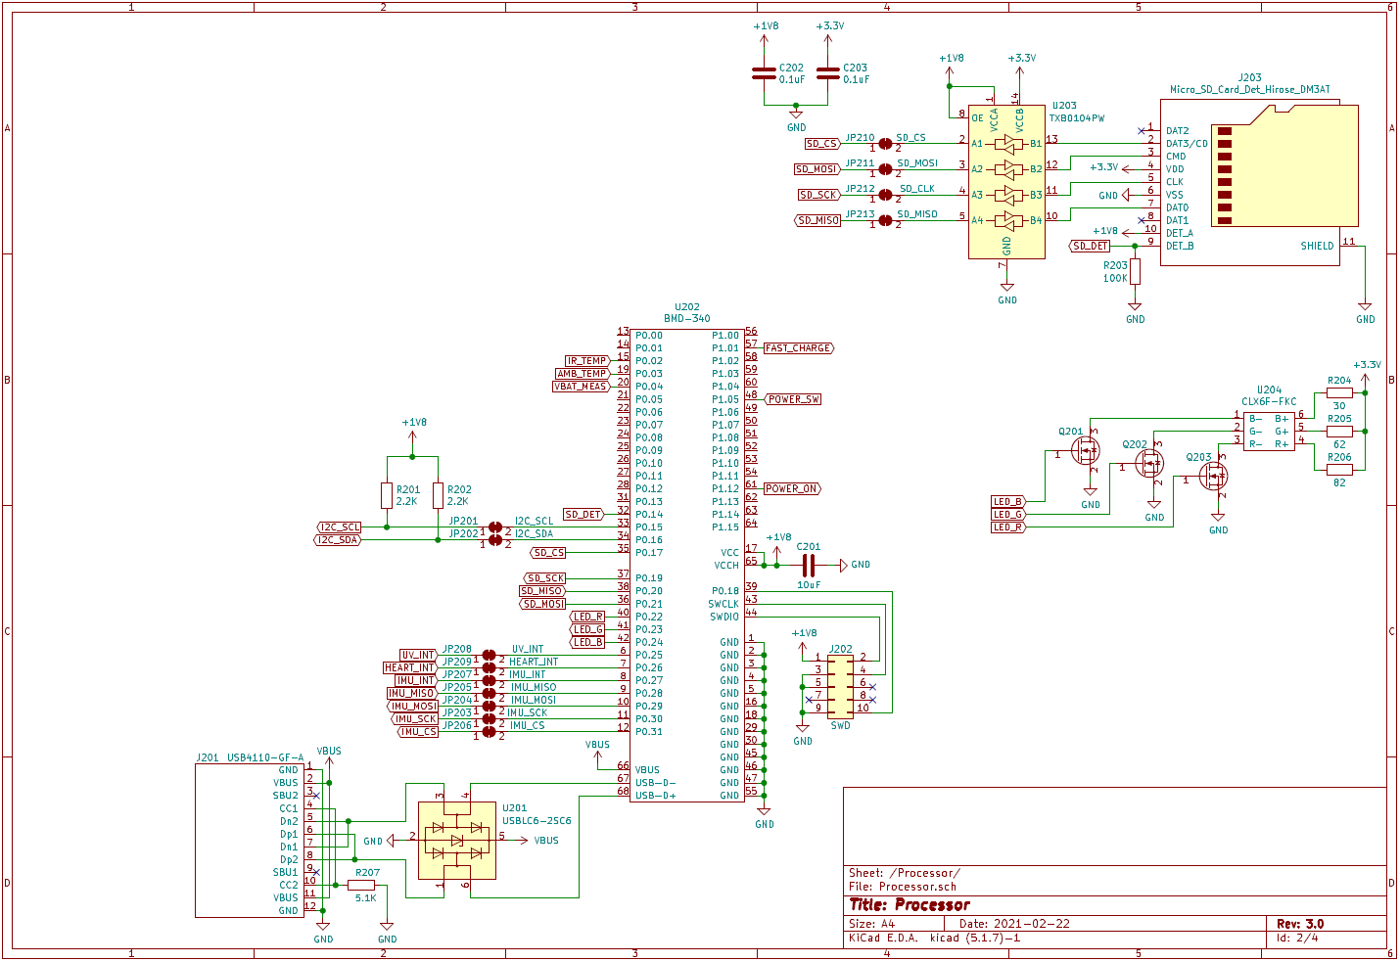
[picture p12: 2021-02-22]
final_report/images/Schematic_REV3_Processor.PNG

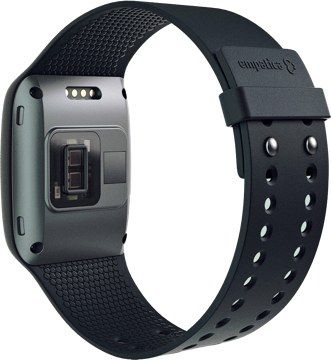
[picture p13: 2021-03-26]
final_report/images/EmpaticaE4.jpg

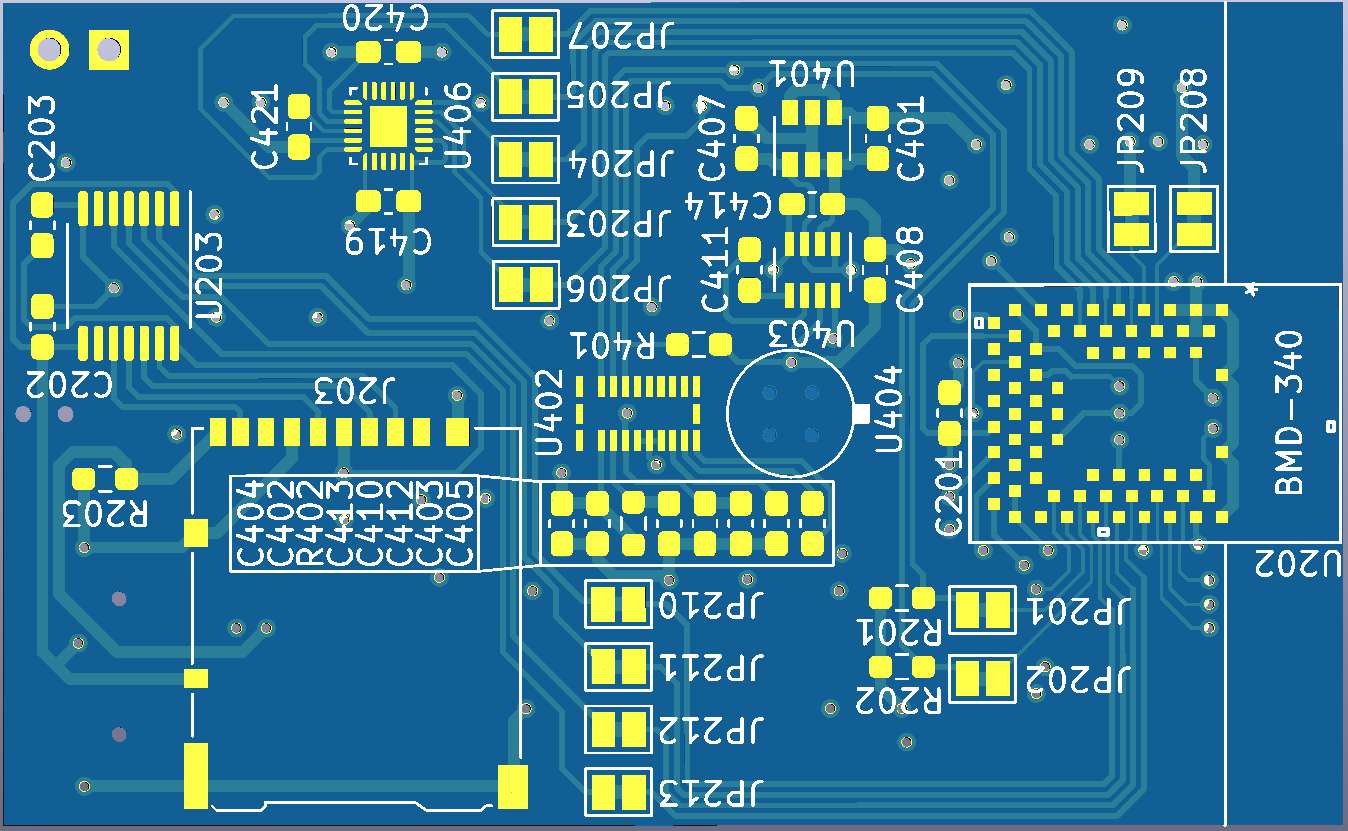
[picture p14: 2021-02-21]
final_report/images/Board_Bottom.png

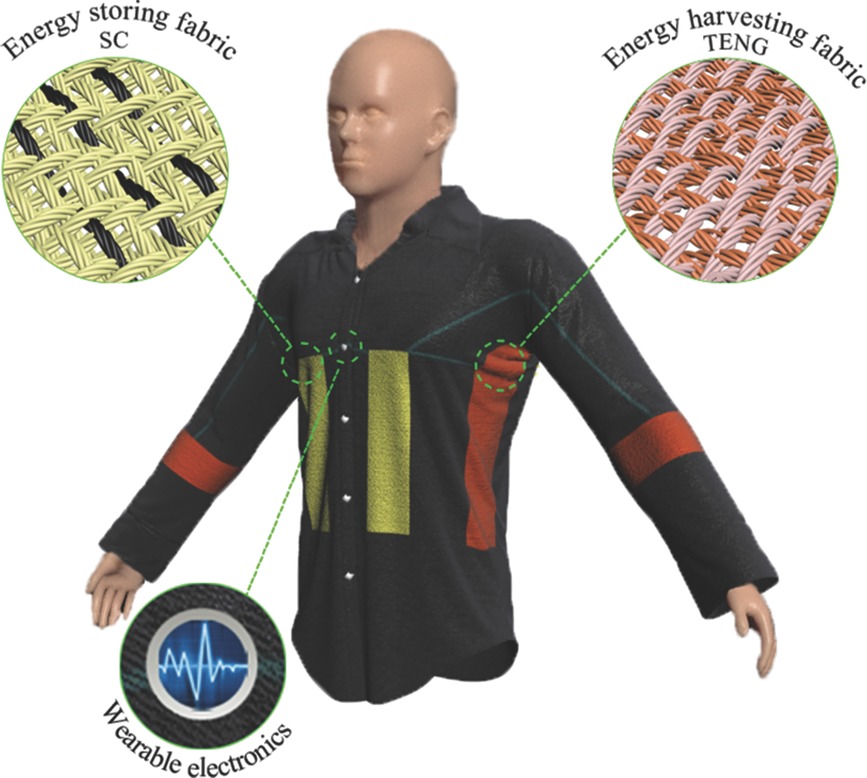
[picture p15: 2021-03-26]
final_report/images/EnergyFabric.jpg

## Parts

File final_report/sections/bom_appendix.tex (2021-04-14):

\begin{center}
{
\tiny
\begin{longtable}{r|>{\raggedright}p{3cm}|>{\raggedright}p{2.5cm}|>{\raggedright}p{3cm}|>{\raggedright}p{3cm}l}
\toprule
Quantity & Description & Manufacturer & Manufacturer Part Number & Digi-Key Part Number \tabularnewline
\midrule
2 & Capacitor: 22pF, 0603 & Samsung Electro-Mechanics & CL10C220JB8NNNC & 1276-1023-1-ND \tabularnewline
1 & Capacitor: 0.01uF, 0603 & Samsung Electro-Mechanics & CL10B103KB8NNNC & 1276-1009-1-ND \tabularnewline
16 & Capacitor: 0.1uF, 0603 & Samsung Electro-Mechanics & CL10B104KB8NNNC & 1276-1000-1-ND \tabularnewline
4 & Capacitor: 1uF, 0603 & Samsung Electro-Mechanics & CL10A105KA8NNNC & 1276-1102-1-ND \tabularnewline
1 & Capacitor: 4.7µF, 0603 & Samsung Electro-Mechanics & CL10A475KP8NNNC & 1276-1044-1-ND \tabularnewline
10 & Capacitor: 10uF, 0603 & Samsung Electro-Mechanics & CL10A106KP8NNNC & 1276-1192-1-ND \tabularnewline
 &  &  &  &  \tabularnewline
1 & Resistor: 4.7 Ω,  0603 & Vishay Dale & CRCW06034R70FKEA & 541-4.70HHCT-ND \tabularnewline
1 & Resistor: 30 Ω,  0603 & Vishay Dale & CRCW060330R0FKEA & 541-30.0HCT-ND \tabularnewline
1 & Resistor: 62 Ω,  0603 & Vishay Dale & CRCW060362R0FKEA & 541-62.0HCT-ND \tabularnewline
1 & Resistor: 82 Ω,  0603 & Vishay Dale & CRCW060382R0FKEA & 541-82.0HCT-ND \tabularnewline
1 & Resistor: 1 KΩ,  0603 & Vishay Dale & CRCW06031K00FKEA & 541-1.00KHCT-ND \tabularnewline
1 & Resistor: 2 KΩ,  0603 & Vishay Dale & CRCW06032K00FKEA & 541-2.00KHCT-ND \tabularnewline
2 & Resistor: 2.2K,  0603 & Vishay Dale & CRCW06032K20FKEA & 541-2.20KHCT-ND \tabularnewline
6 & Resistor: 10 KΩ,  0603 & Vishay Dale & CRCW060310K0FKEA & 541-10.0KHCT-ND \tabularnewline
11 & Resistor: 100 KΩ,  0603 & Vishay Dale & CRCW0603100KFKEA & 541-100KHCT-ND \tabularnewline
1 & Resistor: 150 KΩ,  0603 & Vishay Dale & CRCW0603150KFKEA & 541-150KHCT-ND \tabularnewline
1 & Resistor: 270 KΩ,  0603 & Vishay Dale & CRCW0603270KFKEA & 541-270KHCT-ND \tabularnewline
1 & Resistor: 300 KΩ,  0603 & Vishay Dale & CRCW0603300KFKEA & 541-300KHCT-ND \tabularnewline
1 & Resistor: 309 KΩ,  0603 & Vishay Dale & CRCW0603309KFKEA & 541-309KHCT-ND \tabularnewline
1 & Resistor: 430 KΩ,  0603 & Vishay Dale & CRCW0603430KFKEA & 541-430KHCT-ND \tabularnewline
1 & Resistor: 976 KΩ,  0603 & Vishay Dale & CRCW0603976KFKEA & 541-976KHCT-ND \tabularnewline
 &  &  &  &  \tabularnewline
2 & Inductor: 2.2uH & Taiyo Yuden & NR3012T2R2M & 587-1642-1-ND \tabularnewline
1 & Inductor: 4.7uH & Taiyo Yuden & NR3012T4R7M & 587-1643-1-ND \tabularnewline
 &  &  &  &  \tabularnewline
2 & Schottky diode: 30 V, 500 mA & ON Semiconductor & NSR0530HT1G & NSR0530HT1GOSCT-ND \tabularnewline
1 & USB-C Connector & GCT & USB4110-GF-A & 2073-USB4110-GF-A-1-ND \tabularnewline
1 & Header: 10 Position, 2 Rows, 1.27 mm pitch & Samtec Inc. & FTSH-105-01-L-DV & SAM1161-05-ND \tabularnewline
1 & Micro SD Card Socket & Hirose Electric Co Ltd & DM3AT-SF-PEJM5 & HR1964CT-ND \tabularnewline
5 & N-Channel MOSFET: 20 V, 630 mA & Diodes Incorporated & DMG1012T-7 & DMG1012T-7DICT-ND \tabularnewline
1 & P-Channel MOSFET: 20 V, 460 mA & Diodes Incorporated & DMG1013T-7 & DMG1013T-7DICT-ND \tabularnewline
1 & Tactile Switch (side actuated) & Panasonic Electronic Components & EVQ-P7C01P & P16765CT-ND \tabularnewline
1 & TVS Diode (USB protection) & STMicroelectronics & USBLC6-2SC6 & 497-5235-1-ND \tabularnewline
1 & NRF52840 Module & U-Blox & BMD-340-A-R & 672-BMD-340-A-RCT-ND \tabularnewline
1 & Bidirectional Voltage Level Translator & Texas Instruments & TXB0104PWR & 296-21929-1-ND \tabularnewline
1 & RGB LED & Cree Inc. & CLX6F-FKC-CKNNQDGBB7A363 & CLX6F-FKC-CKNNQDGBB7A363CT-ND \tabularnewline
1 & Single Cell Li-Ion Charge Controller & Microchip Technology & MCP73871-2CCI/ML & MCP73871-2CCI/ML-ND \tabularnewline
2 & Buck Regulator & Diodes Incorporated & AP3401KTTR-G1 & AP3401KTTR-G1DICT-ND \tabularnewline
1 & Boost Regulator & Microchip Technology & MCP1640BT-I/CHY & MCP1640BT-I/CHYCT-ND \tabularnewline
1 & Voltage Reference: 1.024 V & Microchip Technology & MCP1501T-10E/CHY & MCP1501T-10E/CHYCT-ND \tabularnewline
1 & Optical Heart Rate Sensor & Maxim Integrated & MAX86150EFF+T & MAX86150EFF+TCT-ND \tabularnewline
1 & Instrumentation Amplifier & Analog Devices Inc. & AD8293G80ARJZ-R7 & AD8293G80ARJZ-R7CT-ND \tabularnewline
1 & Infrared Temperature Sensor & Amphenol Advanced Sensors & ZTP-148SR & 235-1464-ND \tabularnewline
1 & Air Quality Sensor & Bosch Sensortec & BME680 & 828-1077-1-ND \tabularnewline
1 & 9-Axis IMU & TDK InvenSense & ICM-20948 & 1428-1123-1-ND \tabularnewline
1 & UV Light Sensor & Silicon Labs & SI1133-AA00-GM & SI1133-AA00-GM-ND \tabularnewline
\bottomrule
\end{longtable}
}
\end{center}

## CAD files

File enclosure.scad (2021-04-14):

render_pcb=true;
render_enclosure=true;

// Make the heart rate sensor look more round
$fn = 100;

// Used to prevent 3D geometries that would have zero thickness
nothing = 0.01;


wall_thickness = 1.5;
bottom_thickness = 2.9;
top_thickness = 3;

pcb_size = [57, 35, 1.6];

x_overextrusion = 0.2;

outer_size = [pcb_size.x + wall_thickness * 2 + x_overextrusion * 2,
              pcb_size.y + wall_thickness * 2 + x_overextrusion * 2,
              bottom_thickness + pcb_size.z + top_thickness];

inner_offset = wall_thickness + x_overextrusion;

nub_size = [5, 5, 5];

temperature_diameter = 5.4;
temperature_height = 2.9;
temperature_position = [33.5, 17.5, -temperature_height];

// item[0] - position
// item[1] - size
// item[2] - color
heart_rate = [[24, 15.5, -1.3], [6.1+1, 3.8, 1.3], "hotpink"];
sd_card = [[7, 17.5, -2], [16, 17.5, 2], "silver"];
usb = [[0, 23, pcb_size.z], [7, 10, 4], "gray"];
jumpers = [[23, pcb_size.y-11, -2], [5, 11, 2], "white"];
nrf = [[pcb_size.x-20, (pcb_size.y-11)/2, -2], [20, 11, 2], "yellow"];
jst_pins = [[0, 0, -2], [7, 4, 2], "white"];
resistors = [[sd_card[0].x+sd_card[1].x, jumpers[0].y-4, -1], [13, 4, 1], "white"];
something =  [[30, 3, -1], [8, 10, 1], "white"];
blah =  [[0, 6, -1], [9, 10, 1], "white"];
bleh =  [[30, 3, -1], [8, 10, 1], "white"];
blbh =  [[11, 0, -1], [8, 11, 1], "white"];

// cube_cutouts[0] - position
// cube_cutouts[1] - size
cube_cutouts =
    [
     // Heart Rate Sensor
     [[heart_rate[0].x, heart_rate[0].y, heart_rate[0].z - bottom_thickness],
      [heart_rate[1].x, heart_rate[1].y, heart_rate[1].z + bottom_thickness + nothing]],

     // SD Card
     [sd_card[0],
      [sd_card[1].x, sd_card[1].y + wall_thickness + nothing, sd_card[1].z + nothing]],

     // USB
     [[usb[0].x - (wall_thickness + nothing), usb[0].y, usb[0].z],
      [usb[1].x + (wall_thickness + nothing), usb[1].y, usb[1].z]],

     // Jumpers
     [jumpers[0],
      [jumpers[1].x, jumpers[1].y, jumpers[1].z + nothing]],

     // NRF
     [nrf[0],
      [nrf[1].x, nrf[1].y, nrf[1].z + nothing]],

     [jst_pins[0],
      [jst_pins[1].x, jst_pins[1].y, jst_pins[1].z + nothing]],

     [resistors[0],
      [resistors[1].x, resistors[1].y, resistors[1].z + nothing]],

     [something[0],
      [something[1].x, something[1].y, something[1].z + nothing]],

     [blah[0],
      [blah[1].x, blah[1].y, blah[1].z + nothing]],

     [bleh[0],
      [bleh[1].x, bleh[1].y, bleh[1].z + nothing]],

     [blbh[0],
      [blbh[1].x, blbh[1].y, blbh[1].z + nothing]],

     ];

// A set of two spaced nubs that can hold a watch pin
module watch_nubs(strap_width=20, pin_hole_diameter=1.5) {
    module nub() {
        translate([strap_width/2, 0, 0])
        difference() {
            cube(nub_size);
            translate([-nothing, nub_size.y/2, nub_size.z/2])
                rotate(90, [0, 1, 0])
                linear_extrude(height = nub_size.x/2 + nothing)
                circle(d = pin_hole_diameter, $fn=50);
        }
    }
    nub();
    mirror([1, 0, 0]) nub();
}

// Cutouts for components
module enclosure_cutouts() {
    for(args = cube_cutouts) {
        translate([args[0].x - x_overextrusion,
                   args[0].y - x_overextrusion,
                   args[0].z])
            cube([args[1].x + x_overextrusion*2,
                  args[1].y + x_overextrusion*2,
                  args[1].z]);
    }

    // Temperature
    translate([temperature_position.x,
               temperature_position.y,
               temperature_position.z-bottom_thickness])
        cylinder(d = temperature_diameter + x_overextrusion*2,
                 h = temperature_height+bottom_thickness+nothing);
}

module enclosure_body() {
    difference(){
        cube(outer_size);
        translate([wall_thickness, wall_thickness, bottom_thickness])
            cube([pcb_size.x+x_overextrusion*2, pcb_size.y+x_overextrusion*2, 100]);
        translate([inner_offset, inner_offset, bottom_thickness])
            enclosure_cutouts();
    }
    // TODO
    translate([outer_size.x/2, -nub_size.y, 0])
        watch_nubs();
    translate([outer_size.x/2, outer_size.y, 0])
        watch_nubs();
}

module main_board() {
    components = [heart_rate, sd_card, usb, jumpers, nrf, jst_pins, resistors, something, blah, bleh, blbh];
    for(component = components) {
        color(component[2])
            translate(component[0])
                cube(component[1]);
    }

    // Main pcb
    color("green")
        cube(pcb_size);

    // Temperature
    color("red")
        translate(temperature_position)
            cylinder(d = temperature_diameter, h = temperature_height);
}

if(render_enclosure) {
    enclosure_body();
 }

if(render_pcb) {
    translate([inner_offset, inner_offset, bottom_thickness])
        main_board();
 }

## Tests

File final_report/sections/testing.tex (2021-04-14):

\subsection{Integration Testing}

Through our system's command line interface several intergration tests can be
run. These simple tests print out information that has been collected by sensors
for manual verification. Our command line interface can also be used to inspect
the contents of the attached SD card to verify the operation of the data logging
system.

Our data logging system can also be verified using our companion application,
which is designed to inform the user of invalid input that has been recorded to
the SD card.

\subsection{Performance Measurements}

We made a number of timing measurements for various properties of our firmware
in order to get an understanding of whether our system is able to consistently
meet its timing requirements.

Measurements where taken using a hardware timer configured to run at 8 MHz. Code
to start the timer and code to stop the timer and store the current count was
added in places of interest. For each of the measured quantities 4096 samples
were recorded.

Table \ref{table:timing-results} shows the results of our timing measurements.
For each result the mean value of all recorded samples is given as well as the
standard deviation, and maximum recorded value. For many of the recorded values
almost all of the samples were within a very small range with only a handful
of outliers, because of this a 98th percentile of deviation value is given for
each measured quantity which gives the offset from the mean in which 98\% of the
samples fall.

Later in this section some of the more illuminating measurements are described
in detail.

\begin{longtable}{>{\centering\arraybackslash}m{3.1cm}|
                >{\centering\arraybackslash}m{2.2cm}|
                >{\centering\arraybackslash}m{3.5cm}|
                >{\centering\arraybackslash}m{1.8cm}|
                >{\centering\arraybackslash}m{2.2cm}}
\toprule
Test & Mean Time & 98th Percentile of Deviation & Standard Deviation &
Maximum \\
\midrule
Time between system ticks (millis)  & 998.868 microseconds & 98\% of results
within 250 nanoseconds of the mean & 1.185e-5 & 1.077 milliseconds \\
Time spent executing body of main loop & 5.625 microseconds & 98\% of results
within 16 microseconds of the mean & 6.327e-4 & 35.071 milliseconds \\
Time spend sleeping per iteration of main loop & 931.475 microseconds & 98\% of
results are within 872 microseconds of the mean & 2.14e-4 & 994.624 microseconds
\\
Time to perform a filesystem write operation & 16.722 milliseconds & 98\% of
results are within 31.5 microseconds of the mean & 1.362e-4 & 270.318
milliseconds \\
Time between data-logging write operations & 1.196 seconds & 98\% of results are
within 32 milliseconds of the mean & 9.156e-3 & 1.378 seconds \\
Time to perform an ADC sweep (tigger to data logging call) & 154.842
microseconds & 98\% of results are within 9 microseconds of the mean & 3.359e-4
& 14 milliseconds \\
Time between ADC interrupt and handling of ADC results in main loop & 17.435
microseconds & 98\% of results are within 13 microseconds of the mean &
4.171e-4 & 15.854 milliseconds \\
Time to retrieve IMU sample & 42.009 microseconds & 98\% of results are within
1.25 microseconds of the mean & 2.801e-5 & 1 millisecond \\
Time between IMU samples & 101.059 milliseconds & 98\% of results are within
60.25 microseconds of the mean & 3.005e-3 & 288.711 milliseconds \\
\bottomrule

\caption{Timing Results}
\label{table:timing-results}
\end{longtable}

\subsubsection{System Tick}

The timing results show that our system tick, which is use to maintain a count
of milliseconds ('millis'), is reasonably accurate and precise.

While the average period between SysTick interrupts is slightly less then the 1
millisecond target, the count is very precise. All of the measured samples were
within 750 microseconds of the mean value and 99\% of them where within 375
nanoseconds of the mean which indicates that there is very little jitter in our
millis value.

It is also important to note that for those samples which fell further from the
mean we generally see a delayed interrupt which is immediately followed by a
shorter interrupt period, so over time the average millisecond period remains
accurate even when there is some jitter. This happens because the SysTick timer
is configured in free running mode where it is automatically cleared after each
period and continues counting without needing to be restarted in the SysTick
interrupt handler.

\subsubsection{Data-logging}
\label{subsec:testing-data-logging}

Writes to the SD card are the longest blocking operation that happens in the
main loop. On average, a write operation takes about 16.7 milliseconds, but this
is far from the whole picture.

Figure \ref{fig:write-op-hist} is a histogram showing the distribution of write
operation lengths. To make the histogram legible the data has been trimmed to
remove outliers. Only samples within the 98th percentile of deviation where
kept, leaving 4014 samples in the dataset.

\begin{figure}[!htb]
\centering

\begin{gnuplot}[terminal=pdf,terminaloptions=color]
set xlabel "Length of write operation (s)"
set ylabel "Number of occurrences"

Min = 0.00709125 # where binning starts
Max = 0.037765875 # where binning ends
n = 100 # the number of bins

width = (Max-Min)/n
bin(x) = width*(floor((x-Min)/width)+0.5) + Min

unset key
set style fill solid 0.5
set xrange [Min:Max]

plot 'data/data_log_write_trimmed' using (bin($2)):(1.0) smooth freq with boxes
\end{gnuplot}

\caption{Distribution of filesystem write operation lengths.}
\label{fig:write-op-hist}
\end{figure}

The majority of filesystem write operations take about 12.7 milliseconds, but
the distribution is multimodal and there are also a number of write operations
that take between 25 and 30 milliseconds and around 35 milliseconds. The large
number of writes that take around 12.7 milliseconds are single block writes, the
other groups of write times are 2 and 3 block write operations. This timing data
shows that most of the write operations to the SD card only need to update a
single block, but that occasionally it is necessary to update 2 or 3 blocks at
once.

\subsubsection{Main Loop}

The loop body is made up of a number of service functions which implement the
various software modules that make up the system. Ideally the main loop would
run frequently in order to provide a responsive system. This cooperative
multitasking scheme relies on each of the modules not to block for long periods
in the main loop.

For the most part the loop is very short. The vast majority of loop iterations
measured (more than 90\%) took about 5.5 microseconds. These would be loop
iterations where none of the service functions had any work to do.

Similarly, for about 90\% of loop iterations the processor spends approximately
1 millisecond sleeping. This indicates that interrupt source which wakes the
processor most frequently is the SysTick timer that is used to generate
interrupts every millisecond.

The fact that so many iterations are not performing any work is a sign that the
processor is being woken more often than it needs to be. It would likely we
worth investigating alternative ways of generating our system time value other
than with regular SysTick interrupts such as using a hardware RTC in order to
reduce how often the processor is woken.

\subsubsection{Sensor Sampling}

ADC sweeps were generally quite quick. In over 99\% of measurements the time
from when the sweep was triggered to when the results where processed was only
about 155 microseconds. The time from ADC interrupt to ADC results processing
in the main loop was less than 30 microseconds in 99\% of measurements.

There were however some outliers where ADC sweeps took significantly longer.
The longest delay between ADC interrupt and the results being processed in the
main loop was about 15.8 milliseconds. This time happens to correspond with the
delay for a single block write to the SD card and it is likely that in these
outlier cases the ADC interrupt occurred while a block write was in progress.
This implies that we could see delays of up to around 38 milliseconds in
processing ADC data, but this is not a large concern because our ADC sampling
rate is quite low.

For the IMU, the time required to read a sample from the IMU was measured. This
non-blocking operation is spread out across several iterations of the main loop.
The operation started, then later calls to the IMU service function check
whether it has completed.

In all but a handful of samples it took about 42 microseconds to read a sample
from the IMU. In the remaining samples it took slightly more than a millisecond.
These longer sample occur when the interrupt at the end of the SPI transaction
occurs while the CPU is running code in the main loop after the IMU service
function has been called. In these cases the processor will sleep again before
starting at the top of the main loop and reaching the IMU service function.

These slightly delayed IMU read operations are not a large concern to us, the
IMU sample rate is low enough that a millisecond delay will not cause us to
miss a sample and since the IMU read operation is non-blocking it does not delay
anything else happening in the main loop.

What is more concerning is the possibility of an IMU sample being delayed by
coinciding with an SD card write operation. While we did not see this in our
testing, it remains a theoretical possibility and could cause IMU samples to be
significantly delayed. It would likely be worth investigating ways to make the
SD card write operations non-blocking so that they do not interfere with other
services in the main loop.

\subsection{Power Measurements}

Electrical specifications for the wearable device are shown in Table \ref{table:elec-spec}.
This table includes expected battery charging times, battery life, and current 
consumption under various conditions. All current measurements are shown as an 
expected load on a fully charged battery. As the battery voltage decreases, the
current consumption will increase in order to maintain correct system voltages 
through a DC-DC conversion process.

The quiescent current refers to the current consumption of the device while 
it is turned off. The minimum operating current refers to the minimum current 
required to power up the device without it performing any useful functions. 
The typical operating current refers to the average current the device would 
consume when logging sensor data but not performing any communication. This is 
the condition the device would normally be in while a user is wearing it. The 
remaining current measurements are intermittent and apply only in specific 
situations, and only for the durations that those situations exist. For example, 
the indicator LED current is 15 mA only while the indicator LED is on and the 
colour is red. Several of these currents can be added together with the minimum 
operating current to estimate what the current consumption would be under 
different circumstances. If all three indicator LEDs are on, then the total 
device current can be estimated to be about 15mA (Red LED) + 10mA (Green LED) 
+ 10mA (Blue LED) + 3mA (Minimum Operating Current) = 38mA.

\begin{table*}[!htb]
\centering
\begin{tabular}{>{\centering\arraybackslash}m{6.0cm}|
                >{\centering\arraybackslash}m{4.6cm}|
                >{\centering\arraybackslash}m{1.0cm}|
                >{\centering\arraybackslash}m{1.2cm}}
\toprule
Parameter & Condition & Value & Unit \\
\midrule
Battery Capacity & & 400 & mAh \\
Battery Voltage & Nominal & 3.7 & V \\
Battery Charging Time & Slow charging & 5 & hours \\
Battery Charging Time & Fast charging & 1 & hours \\
Battery Life & Powered off & 6 & months \\
Battery Life & Normal operation & 2 & days \\
Quiescent Current & Powered off, battery voltage = 3.7V & 60 & {\textmu}A \\
Minimum Operating Current & Not collecting data, not communicating, battery voltage = 3.7V & 3 & mA \\
Typical Operating Current & Logging data, not communicating, battery voltage = 3.7V & 7.2 & mA \\
Indicator LED Current & Red only, battery voltage = 3.7V & 15 & mA \\
Indicator LED Current & Green only, battery voltage = 3.7V & 10 & mA \\
Indicator LED Current & Blue only, battery voltage = 3.7V & 10 & mA \\
Bluetooth Transmitting & Battery voltage = 3.7V & 5 & mA \\
Bluetooth Receiving & Battery voltage = 3.7V & 3 & mA \\
SD Card Current & Battery voltage = 3.7V & 2 & mA \\
Heart Rate Measurement Current & Battery voltage = 3.7V & 375 & {\textmu}A \\
UV Light Measurement Current & Battery voltage = 3.7V & 2 & mA \\
IMU 9-Axis Measurement Current & Battery voltage = 3.7V & 1.5 & mA \\
Temperature Measurement Current & Battery voltage = 3.7V & 625 & {\textmu}A \\
\bottomrule
\end{tabular}
\caption{Electrical Specifications}
\label{table:elec-spec}
\end{table*}

\subsection{Companion App Testing}

Most erroneous cases handled by the companion app are not fatal errors but warnings about skipped data. One example is that if an entry has an unrecognized type such as adding a new sensor then it is skipped and all other recognized entries are still parsed.

One notable case is that if an entry specifies it has a length of 28 bytes then
writes 10 bytes and loses power, upon reset the reset offsets file is updated with 
the length of the file and a reset command is written after the 10 bytes.  
In this case it is desirable to use the offset information in offsets to 
identify that the previous entry was not written in its entirety and discard it without allowing it to corrupt all subsequent entries.  Almost all tests for the companion app test scenarios like this where it is asserted that no fatal error was raised, the expected warning messages were given and all valid data is output as expected. As such there are no test cases to test "totally valid" data.

One case which correspond to fatal errors is when the offset specified by offsets file does not correspond to a reset command, in this case there is nothing reasonable the companion app can do to try to identify entry boundaries from the file so it gives up.  A second case which causes a fatal error is when the CLI returns the string "Failed to open file" when reading the file, as there is nothing that can be done if the SD card is corrupted and the file cannot be read, these are the only 2 fatal error cases that are tested for.

The CLI interaction is tested by creating a mock serial interface which follows the same protocols as the bluetooth or usb serial connection.  The bluetooth connection or USB serial connection are hard to write automated tests for so they are not covered by the test suite.

\subsection{Physical Dimensions}

The BioSense wearable ended up being rather small and lightweight. Although it
is bigger than most watches at 6cm by 4.8cm, it quite comfortably fits on a
wrist. The weight is also very reasonable at 50.4 grams.

\begin{longtable}{ c | c }
\toprule
Quantity & Value \\
\midrule
Weight of assembled circuit boards & 11 grams \\
Weight of enclosure & 7.4 grams \\
Weight of battery & 9 grams \\
Weight of strap & 23 grams \\
Maximum assembled length & 6 cm \\
Maximum assembled width & 4.8 cm \\
Maximum assembled thickness & 1 cm \\
\bottomrule

\caption{Physical Dimensions}
\label{table:physical-dimensions}
\end{longtable}

\subsection{Cost}

Our prototypes cost approximately \$100 to manufacture. We spend \$49.58 on
five copies of our printed circuit board (\$10.10 in manufacturing costs and
\$39.49 in shipping costs). The components for each copy of the board cost
approximately \$88. This does not include the cost of the air quality sensor we 
were planning to use as we where unable to purchase it, the air quality sensor
would added approximately an additional \$15 per copy of the board assembled.

Appendix \ref{sec:appendix-bom} contains a list of components used in the
device.

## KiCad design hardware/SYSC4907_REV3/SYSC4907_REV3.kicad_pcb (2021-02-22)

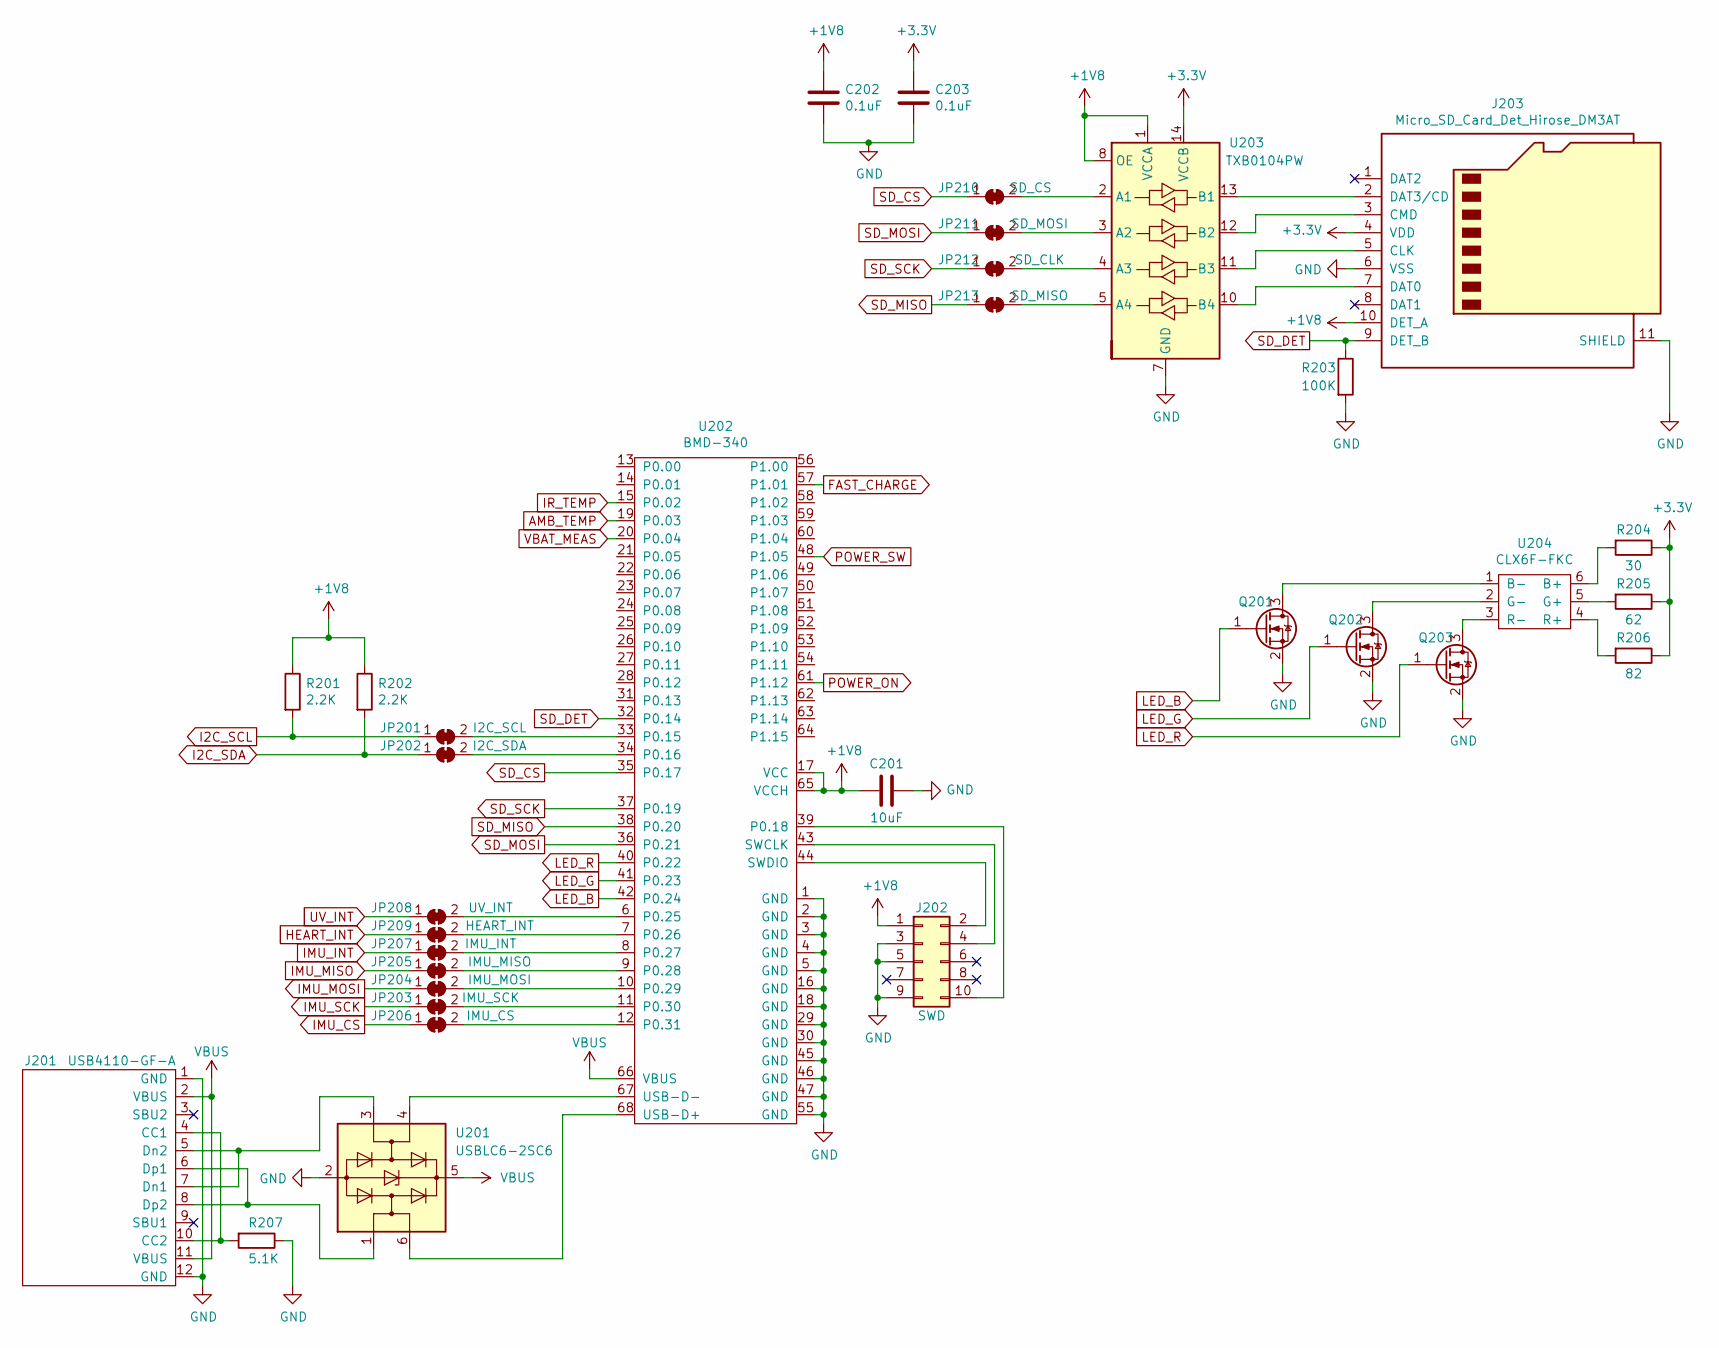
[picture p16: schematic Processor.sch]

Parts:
C201: 10uF; C_0603_1608Metric_Pad1.08x0.95mm_HandSolder
C202, C203: 0.1uF; C_0603_1608Metric_Pad1.08x0.95mm_HandSolder
J201: USB4110-GF-A; MPN USB4110-GF-A
J202: SWD; PinHeader_2x05_P1.27mm_Vertical_SMD; MPN FTS-105-01-L-DV
J203: Micro_SD_Card_Det_Hirose_DM3AT; microSD_HC_Hirose_DM3AT-SF-PEJM5; MPN DM3AT-SF-PEJM5
JP201: I2C_SCL; SolderJumper-2_P1.3mm_Bridged_Pad1.0x1.5mm
JP202: I2C_SDA; SolderJumper-2_P1.3mm_Bridged_Pad1.0x1.5mm
JP203: IMU_SCK; SolderJumper-2_P1.3mm_Bridged_Pad1.0x1.5mm
JP204: IMU_MOSI; SolderJumper-2_P1.3mm_Bridged_Pad1.0x1.5mm
JP205: IMU_MISO; SolderJumper-2_P1.3mm_Bridged_Pad1.0x1.5mm
JP206: IMU_CS; SolderJumper-2_P1.3mm_Bridged_Pad1.0x1.5mm
JP207: IMU_INT; SolderJumper-2_P1.3mm_Bridged_Pad1.0x1.5mm
JP208: UV_INT; SolderJumper-2_P1.3mm_Bridged_Pad1.0x1.5mm
JP209: HEART_INT; SolderJumper-2_P1.3mm_Bridged_Pad1.0x1.5mm
JP210: SD_CS; SolderJumper-2_P1.3mm_Bridged_Pad1.0x1.5mm
JP211: SD_MOSI; SolderJumper-2_P1.3mm_Bridged_Pad1.0x1.5mm
JP212: SD_CLK; SolderJumper-2_P1.3mm_Bridged_Pad1.0x1.5mm
JP213: SD_MISO; SolderJumper-2_P1.3mm_Bridged_Pad1.0x1.5mm
Q201, Q202, Q203: DMG1012T; SOT-523; MPN DMG1012T
R201, R202: 2.2K; R_0603_1608Metric_Pad0.98x0.95mm_HandSolder
R203: 100K; R_0603_1608Metric_Pad0.98x0.95mm_HandSolder
R204: 30; R_0603_1608Metric_Pad0.98x0.95mm_HandSolder
R205: 62; R_0603_1608Metric_Pad0.98x0.95mm_HandSolder
R206: 82; R_0603_1608Metric_Pad0.98x0.95mm_HandSolder
R207: 5.1K; R_0603_1608Metric_Pad0.98x0.95mm_HandSolder
U201: USBLC6-2SC6; SOT-23-6; MPN USBLC6-2SC6
U202: BMD-340; BMD-340-A-R; MPN BMD-340
U203: TXB0104PW; TSSOP-14_4.4x5mm_P0.65mm; MPN TXB0104PW
U204: CLX6F-FKC; MPN CLX6F-FKC

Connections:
+1V8: C201.2, C202.1, J202.1, J203.10 (DET_A), R201.1, R202.1, U202.17 (VCC), U202.65 (VCCH), U203.1 (VCCA), U203.8 (OE); also elsewhere on the board
+3V3: C203.1, J203.4 (VDD), R204.1, R205.1, R206.1, U203.14 (VCCB); also elsewhere on the board
AMB_TEMP: U202.19 (P0.03); also elsewhere on the board
FAST_CHARGE: U202.57 (P1.01); also elsewhere on the board
GND: C201.1, C202.2, C203.2, J201.1 (GND), J201.12 (GND), J202.3, J202.5, J202.9, J203.6 (VSS), J203.11 (SHIELD), Q201.2 (S), Q202.2 (S), Q203.2 (S), R203.2, R207.1, U201.2 (GND), U202.1 (GND), U202.2 (GND), U202.3 (GND), U202.4 (GND), U202.5 (GND), U202.16 (GND), U202.18 (GND), U202.29 (GND), U202.30 (GND), U202.45 (GND), U202.46 (GND), U202.47 (GND), U202.55 (GND), U203.7 (GND); also elsewhere on the board
HEART_INT: JP209.1 (A); also elsewhere on the board
I2C_SCL: JP201.1 (A), R201.2; also elsewhere on the board
I2C_SDA: JP202.1 (A), R202.2; also elsewhere on the board
IMU_CS: JP206.1 (A); also elsewhere on the board
IMU_INT: JP207.1 (A); also elsewhere on the board
IMU_MISO: JP205.1 (A); also elsewhere on the board
IMU_MOSI: JP204.1 (A); also elsewhere on the board
IMU_SCK: JP203.1 (A); also elsewhere on the board
IR_TEMP: U202.15 (P0.02); also elsewhere on the board
LED_B: Q201.1 (G), U202.42 (P0.24)
LED_G: Q202.1 (G), U202.41 (P0.23)
LED_R: Q203.1 (G), U202.40 (P0.22)
unnamed: J201.5 (Dn2), J201.7 (Dn1), U201.3 (I/O2)
unnamed: J201.6 (Dp1), J201.8 (Dp2), U201.1 (I/O1)
unnamed: J201.4 (CC1), J201.10 (CC2), R207.2
unnamed: J202.2, U202.44 (SWDIO)
unnamed: J202.4, U202.43 (SWCLK)
unnamed: J202.10, U202.39 (P0.18)
unnamed: J203.2 (DAT3/CD), U203.13 (B1)
unnamed: J203.3 (CMD), U203.12 (B2)
unnamed: J203.5 (CLK), U203.11 (B3)
unnamed: J203.7 (DAT0), U203.10 (B4)
unnamed: JP201.2 (B), U202.33 (P0.15)
unnamed: JP202.2 (B), U202.34 (P0.16)
unnamed: JP203.2 (B), U202.11 (P0.30)
unnamed: JP204.2 (B), U202.10 (P0.29)
unnamed: JP205.2 (B), U202.9 (P0.28)
unnamed: JP206.2 (B), U202.12 (P0.31)
unnamed: JP207.2 (B), U202.8 (P0.27)
unnamed: JP208.2 (B), U202.6 (P0.25)
unnamed: JP209.2 (B), U202.7 (P0.26)
unnamed: JP210.2 (B), U203.2 (A1)
unnamed: JP211.2 (B), U203.3 (A2)
unnamed: JP212.2 (B), U203.4 (A3)
unnamed: JP213.2 (B), U203.5 (A4)
unnamed: Q201.3 (D), U204.1 (B-)
unnamed: Q202.3 (D), U204.2 (G-)
unnamed: Q203.3 (D), U204.3 (R-)
unnamed: R204.2, U204.6 (B+)
unnamed: R205.2, U204.5 (G+)
unnamed: R206.2, U204.4 (R+)
unnamed: U201.4 (I/O2), U202.67 (USB-D-)
unnamed: U201.6 (I/O1), U202.68 (USB-D+)
POWER_ON: U202.61 (P1.12); also elsewhere on the board
POWER_SW: U202.48 (P1.05); also elsewhere on the board
SD_CS: JP210.1 (A), U202.35 (P0.17)
SD_DET: J203.9 (DET_B), R203.1, U202.32 (P0.14)
SD_MISO: JP213.1 (A), U202.38 (P0.20)
SD_MOSI: JP211.1 (A), U202.36 (P0.21)
SD_SCK: JP212.1 (A), U202.37 (P0.19)
UV_INT: JP208.1 (A); also elsewhere on the board
VBAT_MEAS: U202.20 (P0.04); also elsewhere on the board
VBUS: J201.2 (VBUS), J201.11 (VBUS), U201.5 (VBUS), U202.66 (VBUS); also elsewhere on the board

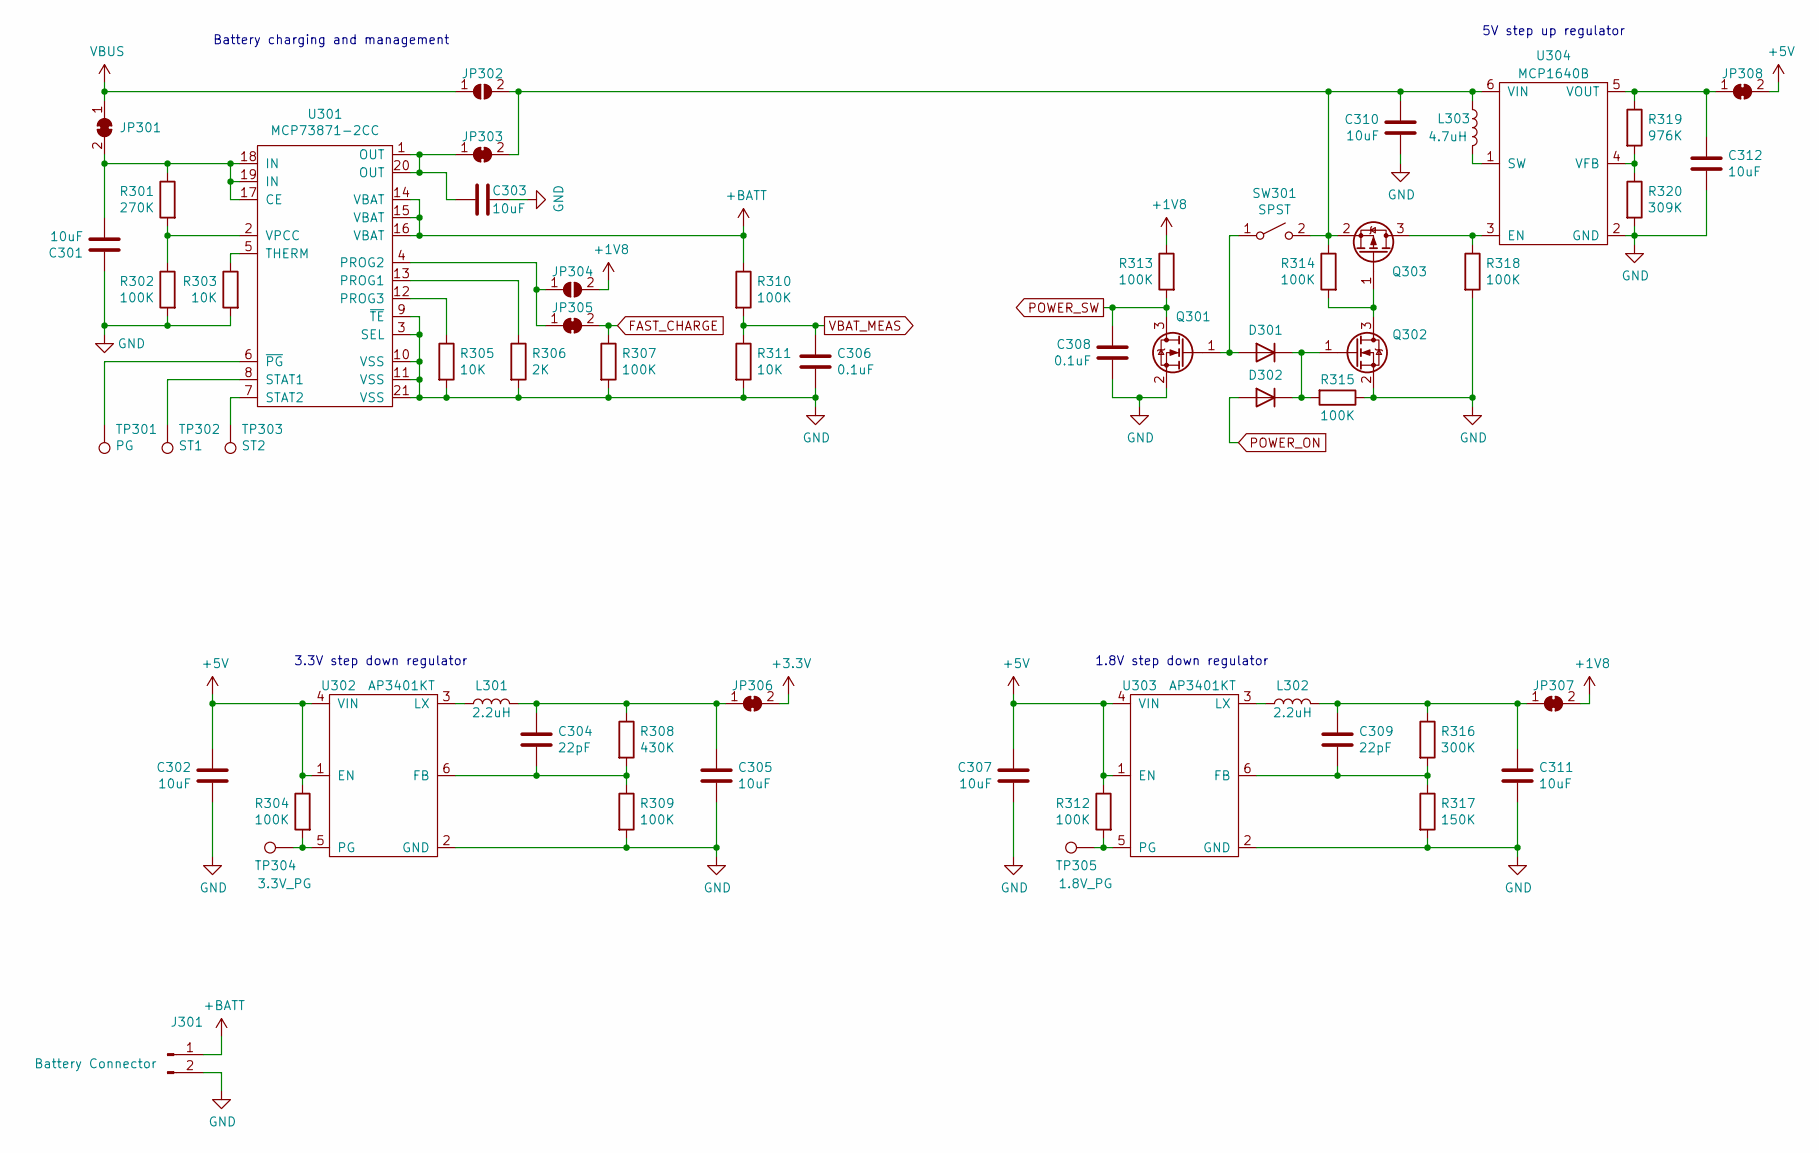
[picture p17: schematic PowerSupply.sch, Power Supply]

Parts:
C301, C302, C303, C305, C307, C310, C311, C312: 10uF; C_0603_1608Metric_Pad1.08x0.95mm_HandSolder
C304, C309: 22pF; C_0603_1608Metric_Pad1.08x0.95mm_HandSolder
C306, C308: 0.1uF; C_0603_1608Metric_Pad1.08x0.95mm_HandSolder
D301, D302: NSR0530HT1G; D_SOD-323_HandSoldering; MPN NSR0530HT1G
J301: Battery Connector; PinHeader_1x02_P2.54mm_Vertical
JP301, JP303, JP305, JP306, JP307, JP308: Bridged; SolderJumper-2_P1.3mm_Bridged_Pad1.0x1.5mm
JP302, JP304: Open; SolderJumper-2_P1.3mm_Open_Pad1.0x1.5mm
L301, L302: 2.2uH; L_Taiyo-Yuden_NR-30xx_HandSoldering; MPN NRH3012T2R2MN
L303: 4.7uH; L_Taiyo-Yuden_NR-30xx_HandSoldering; MPN NRH3012T4R7MN
Q301, Q302: DMG1012T; SOT-523; MPN DMG1012T
Q303: DMG1013T; SOT-523; MPN DMG1013T
R301: 270K; R_0603_1608Metric_Pad0.98x0.95mm_HandSolder
R302, R304, R307, R309, R310, R312, R313, R314, R315, R318: 100K; R_0603_1608Metric_Pad0.98x0.95mm_HandSolder
R303, R305, R311: 10K; R_0603_1608Metric_Pad0.98x0.95mm_HandSolder
R306: 2K; R_0603_1608Metric_Pad0.98x0.95mm_HandSolder
R308: 430K; R_0603_1608Metric_Pad0.98x0.95mm_HandSolder
R316: 300K; R_0603_1608Metric_Pad0.98x0.95mm_HandSolder
R317: 150K; R_0603_1608Metric_Pad0.98x0.95mm_HandSolder
R319: 976K; R_0603_1608Metric_Pad0.98x0.95mm_HandSolder
R320: 309K; R_0603_1608Metric_Pad0.98x0.95mm_HandSolder
SW301: SPST; EVQ-P7C01P; MPN EVQ-P7C01P
TP301: PG; TestPoint_Pad_D1.0mm
TP302: ST1; TestPoint_Pad_D1.0mm
TP303: ST2; TestPoint_Pad_D1.0mm
TP304: 3.3V_PG; TestPoint_Pad_D1.0mm
TP305: 1.8V_PG; TestPoint_Pad_D1.0mm
U301: MCP73871-2CC; QFN-20-1EP_4x4mm_P0.5mm_EP2.7x2.7mm; MPN MCP73871-2CC
U302, U303: AP3401KT; TSOT-23-6; MPN AP3401KT
U304: MCP1640B; SOT-23-6; MPN MCP1640B

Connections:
+1V8: JP304.2 (B), JP307.2 (B), R313.1; also elsewhere on the board
+3V3: JP306.2 (B); also elsewhere on the board
+5V: C302.1, C307.1, JP308.2 (B), R304.1, R312.1, U302.1 (EN), U302.4 (VIN), U303.1 (EN), U303.4 (VIN)
+BATT: J301.1, R310.1, U301.14 (VBAT), U301.15 (VBAT), U301.16 (VBAT)
FAST_CHARGE: JP305.2 (B), R307.1; also elsewhere on the board
GND: C301.1, C302.2, C303.1, C305.2, C306.2, C307.2, C308.2, C310.2, C311.2, C312.2, J301.2, Q301.2 (S), Q302.2 (S), R302.2, R303.2, R305.2, R306.2, R307.2, R309.2, R311.2, R315.1, R317.2, R318.2, R320.2, U301.3 (SEL), U301.9 (~TE), U301.10 (VSS), U301.11 (VSS), U301.21 (VSS), U302.2 (GND), U303.2 (GND), U304.2 (GND); also elsewhere on the board
unnamed: C301.2, JP301.2 (B), R301.1, U301.17 (CE), U301.18 (IN), U301.19 (IN)
unnamed: C303.2, JP303.1 (A), U301.1 (OUT), U301.20 (OUT)
unnamed: C304.1, C305.1, JP306.1 (A), L301.1, R308.1
unnamed: C304.2, R308.2, R309.1, U302.6 (FB)
unnamed: C309.1, C311.1, JP307.1 (A), L302.1, R316.1
unnamed: C309.2, R316.2, R317.1, U303.6 (FB)
unnamed: C310.1, JP302.2 (B), JP303.2 (B), L303.1, Q303.2 (S), R314.1, SW301.2 (B), U304.6 (VIN)
unnamed: C312.1, JP308.1 (A), R319.1, U304.5 (VOUT)
unnamed: D301.1 (K), D302.1 (K), Q302.1 (G), R315.2
unnamed: D301.2 (A), Q301.1 (G), SW301.1 (A)
unnamed: JP304.1 (A), JP305.1 (A), U301.4 (PROG2)
unnamed: L301.2, U302.3 (LX)
unnamed: L302.2, U303.3 (LX)
unnamed: L303.2, U304.1 (SW)
unnamed: Q302.3 (D), Q303.1 (G), R314.2
unnamed: Q303.3 (D), R318.1, U304.3 (EN)
unnamed: R301.2, R302.1, U301.2 (VPCC)
unnamed: R303.1, U301.5 (THERM)
unnamed: R304.2, TP304.1, U302.5 (PG)
unnamed: R305.1, U301.12 (PROG3)
unnamed: R306.1, U301.13 (PROG1)
unnamed: R312.2, TP305.1, U303.5 (PG)
unnamed: R319.2, R320.1, U304.4 (VFB)
unnamed: TP301.1, U301.6 (~PG)
unnamed: TP302.1, U301.8 (STAT1)
unnamed: TP303.1, U301.7 (STAT2)
POWER_ON: D302.2 (A); also elsewhere on the board
POWER_SW: C308.1, Q301.3 (D), R313.2; also elsewhere on the board
VBAT_MEAS: C306.1, R310.2, R311.1; also elsewhere on the board
VBUS: JP301.1 (A), JP302.1 (A); also elsewhere on the board

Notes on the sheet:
3.3V step down regulator
1.8V step down regulator
5V step up regulator
Battery charging and management

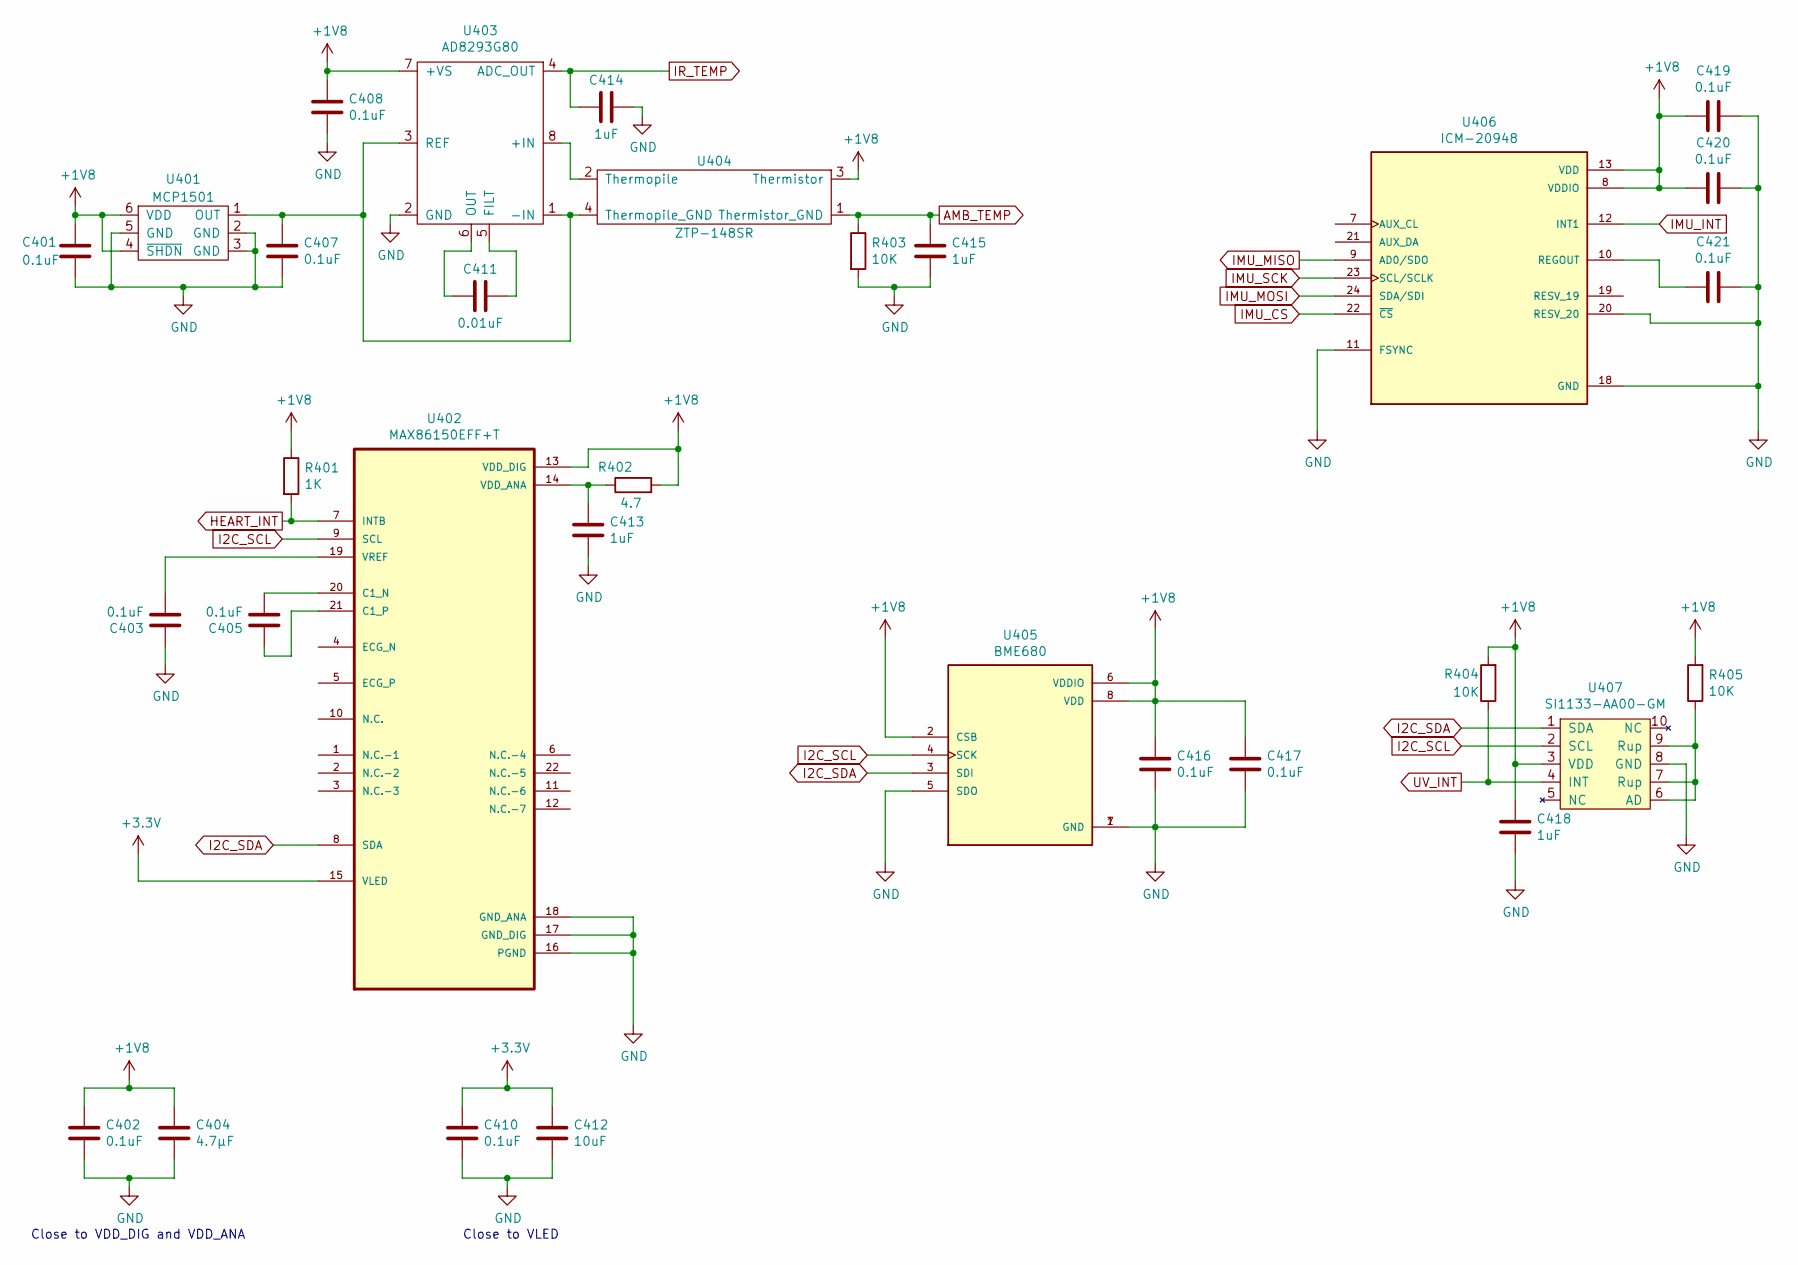
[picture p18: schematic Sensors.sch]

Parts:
C401, C402, C403, C405, C407, C408, C410, C416, C417, C419, C420, C421: 0.1uF; C_0603_1608Metric_Pad1.08x0.95mm_HandSolder
C404: 4.7µF; C_0603_1608Metric_Pad1.08x0.95mm_HandSolder
C411: 0.01uF; C_0603_1608Metric_Pad1.08x0.95mm_HandSolder
C412: 10uF; C_0603_1608Metric_Pad1.08x0.95mm_HandSolder
C413, C414, C415, C418: 1uF; C_0603_1608Metric_Pad1.08x0.95mm_HandSolder
R401: 1K; R_0603_1608Metric_Pad0.98x0.95mm_HandSolder
R402: 4.7; R_0603_1608Metric_Pad0.98x0.95mm_HandSolder
R403, R404, R405: 10K; R_0603_1608Metric_Pad0.98x0.95mm_HandSolder
U401: MCP1501; SOT-23-6; MPN MCP1501T-10E/CHY
U402: MAX86150EFF+T; MPN MAX86150EFF+T
U403: AD8293G80; SOT-23-8; MPN AD8293G80
U404: ZTP-148SR; MPN ZTP-148SR
U405: BME680; Bosch_LGA-8_3x3mm_P0.8mm_ClockwisePinNumbering; MPN BME680
U406: ICM-20948; QFN-24-1EP_3x3mm_P0.4mm_EP1.75x1.6mm; MPN ICM-20948
U407: SI1133-AA00-GM; MPN SI1133-AA00-GM

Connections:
+1V8: C401.1, C402.1, C404.1, C408.1, C416.1, C417.1, C418.2, C419.2, C420.2, R401.1, R402.2, R404.2, R405.2, U401.4 (~SHDN), U401.6 (VDD), U402.13 (VDD_DIG), U403.7 (+VS), U404.3 (Thermistor), U405.2 (CSB), U405.6 (VDDIO), U405.8 (VDD), U406.8 (VDDIO), U406.13 (VDD), U407.3 (VDD); also elsewhere on the board
+3V3: C410.1, C412.1, U402.15 (VLED); also elsewhere on the board
AMB_TEMP: C415.1, R403.1, U404.1 (Thermistor_GND); also elsewhere on the board
GND: C401.2, C402.2, C403.1, C404.2, C407.2, C408.2, C410.2, C412.2, C413.2, C414.1, C415.2, C416.2, C417.2, C418.1, C419.1, C420.1, C421.1, R403.2, U401.2 (GND), U401.3 (GND), U401.5 (GND), U402.16 (PGND), U402.17 (GND_DIG), U402.18 (GND_ANA), U403.2 (GND), U405.1 (GND), U405.5 (SDO), U405.7 (GND), U406.11 (FSYNC), U406.18 (GND), U406.20 (RESV_20), U407.8 (GND); also elsewhere on the board
HEART_INT: R401.2, U402.7 (INTB); also elsewhere on the board
I2C_SCL: U402.9 (SCL), U405.4 (SCK), U407.2 (SCL); also elsewhere on the board
I2C_SDA: U402.8 (SDA), U405.3 (SDI), U407.1 (SDA); also elsewhere on the board
IMU_CS: U406.22 (~CS); also elsewhere on the board
IMU_INT: U406.12 (INT1); also elsewhere on the board
IMU_MISO: U406.9 (AD0/SDO); also elsewhere on the board
IMU_MOSI: U406.24 (SDA/SDI); also elsewhere on the board
IMU_SCK: U406.23 (SCL/SCLK); also elsewhere on the board
IR_TEMP: C414.2, U403.4 (ADC_OUT); also elsewhere on the board
unnamed: C403.2, U402.19 (VREF)
unnamed: C405.1, U402.21 (C1_P)
unnamed: C405.2, U402.20 (C1_N)
unnamed: C407.1, U401.1 (OUT), U403.1 (-IN), U403.3 (REF), U404.4 (Thermopile_GND)
unnamed: C411.1, U403.5 (FILT)
unnamed: C411.2, U403.6 (OUT)
unnamed: C413.1, R402.1, U402.14 (VDD_ANA)
unnamed: C421.2, U406.10 (REGOUT)
unnamed: R405.1, U407.6 (AD), U407.7 (Rup), U407.9 (Rup)
unnamed: U403.8 (+IN), U404.2 (Thermopile)
UV_INT: R404.1, U407.4 (INT); also elsewhere on the board

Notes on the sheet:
Close to VDD_DIG and VDD_ANA
Close to VLED

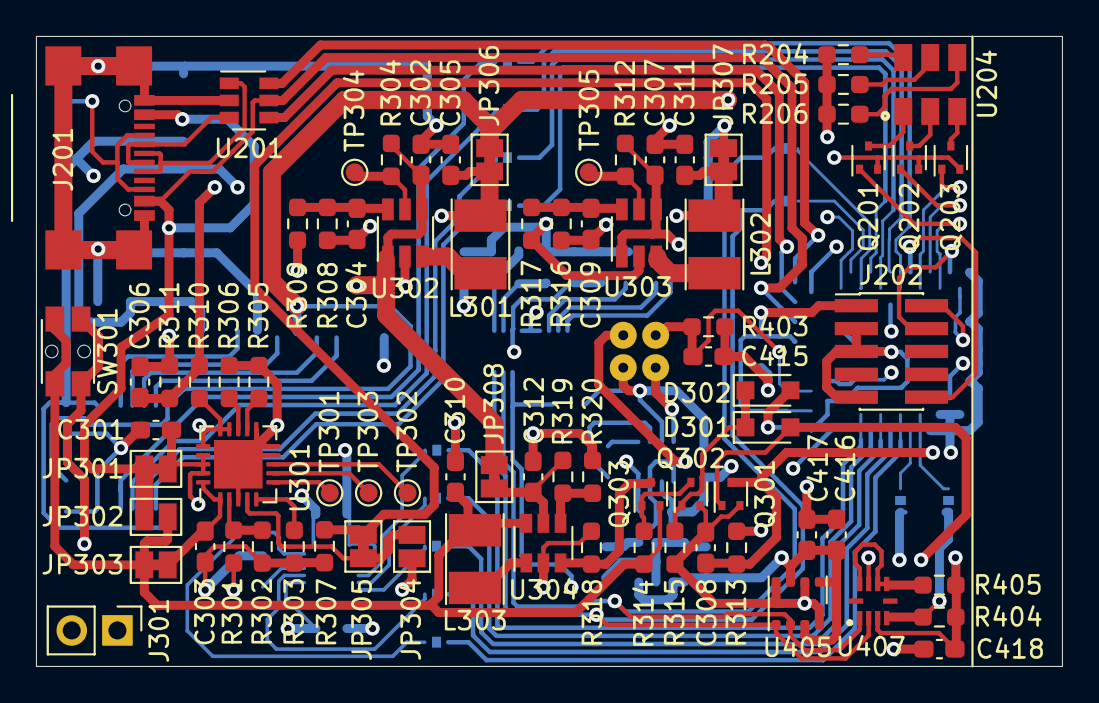
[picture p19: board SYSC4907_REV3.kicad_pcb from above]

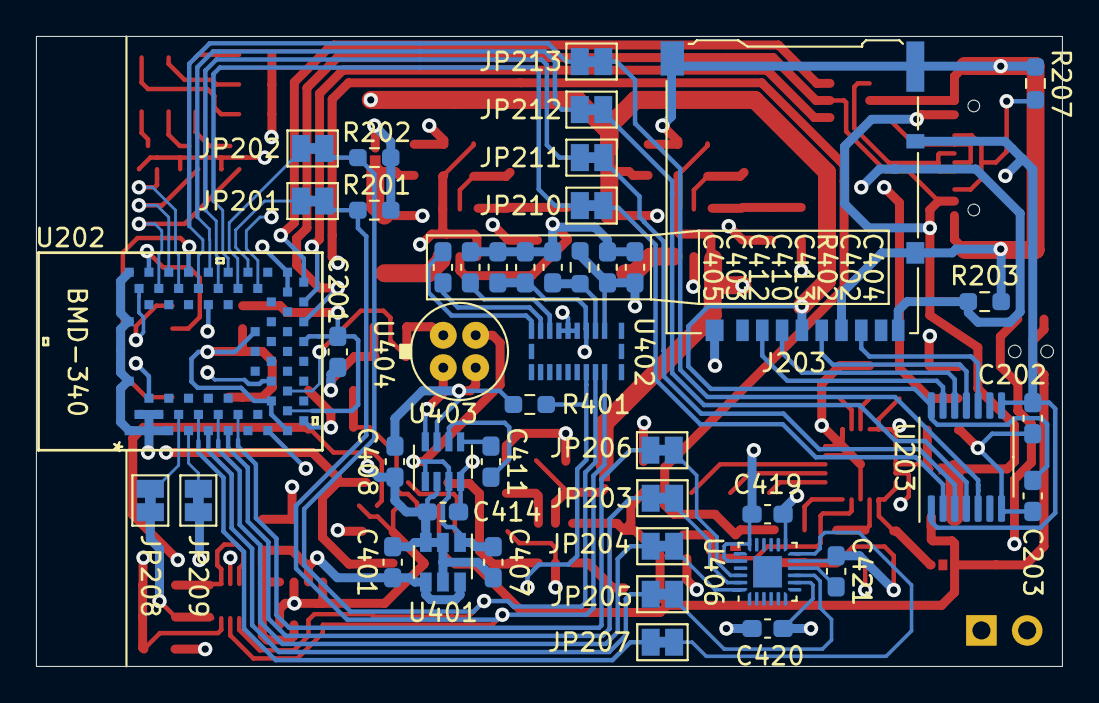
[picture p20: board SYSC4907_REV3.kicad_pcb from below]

Board: 4 copper layers, 57.0 x 35.0 mm, 123 parts (45 on the bottom side), 96 nets.

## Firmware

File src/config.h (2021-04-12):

#ifndef config_h
#define config_h

#include "global.h"
#include "icm_20948.h"

//
//
//  SD Card
//
//
#define ENABLE_SD_CARD

#define SDC_SCK_PIN     19
#define SDC_MOSI_PIN    21
#define SDC_MISO_PIN    20
#define SDC_CS_PIN      17


//
//
//  Bluetooth
//
//
#define ENABLE_BLUETOOTH


//
//
//  IMU
//
//
#define ENABLE_IMU

#define IMU_PERIOD MS_TO_MILLIS(100)

#ifdef ENABLE_IMU
// Sensor driver instances go here so that we can use them in CLI commands
extern struct icm_20948_desc imu;
#endif


//
//
//  ADC
//
//
#define ENABLE_ADC

#define ADC_PERIOD MS_TO_MILLIS(500)


//
//
//  Profiling
//
//
//#define ENABLE_PROFILING

#define PROFILER_NUM_SAMPLES    4096
#define PROFILING_TIMER NRF_TIMER2

#endif /* config_h */

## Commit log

2020-09-26 Update sensors list
2021-01-16 Add initial enclosure model
    [enclosure.scad]
2021-01-21 consolidated variables, added main_board, adjusted values
    [enclosure.scad]
2021-02-19 max86150: change many Arduino things into their c counterpart
    Also replaced tabs with spaces
2021-02-21 add partial work for UV light sensor
2021-02-22 added board designs to repo and made corrections to REV2 schematic and layout
    [PowerSupply.sch, Processor.sch, SYSC4907_REV2-B_Cu.gbr, SYSC4907_REV2-B_Mask.gbr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]
2021-02-22 added updated schematics and board design to appendices, and updated overview
    [SYSC4907_REV3.kicad_pcb]
2021-02-27 final report: copy enclosure section from proposal verbatim
2021-02-27 enclosure: make nub position dependent on nub size
    [enclosure.scad]
2021-02-27 enclosure: add top_thickness variable
    [enclosure.scad]
2021-02-27 enclosure: make global variables for component size and location
    [enclosure.scad]
2021-02-27 enclosure: add cutouts for sensors, USB, and SD card
    [enclosure.scad]
2021-02-27 final report: Add enclosure render
2021-02-27 final report (enclosure): change tense to past tense
2021-02-28 final report: add assembly and parts availability challenges
2021-02-28 final report (enclosure appendix): Fix formatting
2021-03-01 final report: add photos of board
2021-03-01 final report (enclosure): change me to us
2021-03-01 final report: adjust size of board photos to avoid mostly blank page
2021-03-08 fix zero thickness geometries in enclosure
    [enclosure.scad]
2021-03-08 add script to generate enclosure renders
    [enclosure.scad]
2021-03-14 Add time command for logging current unix time
2021-03-14 added temp and voltage log structs
2021-03-16 Enclosure changes
    refactored code
    added x_overextrusion variable
    added more cutouts
    [enclosure.scad]
2021-03-19 update enclosure
    [enclosure.scad]
2021-03-20 enclosure updates
    [enclosure.scad]
2021-04-10 Fix names of ICM20948 pin constants to say SPI instead of I2C
2021-04-12 Rearrange sections
    Abstract is now after the title page
    Enclosure is now part of hardware
2021-04-13 Add integration testing content and board weight to final report testing section
2021-04-14 final report: Update enclosure section
2021-04-14 final enclosure changes
    [enclosure.scad]
2021-04-14 updated info about sensors completed in all three places
2021-04-14 macro for cost of board
2021-04-14 fix companion app flow chart size
2021-04-14 abstract and intro for sensor descriptions also future tence for solutions section, still uses "will" in a case which is not specifically future tense, think it is fine.
    also plot file for video
2021-04-14 Update board cost in final report

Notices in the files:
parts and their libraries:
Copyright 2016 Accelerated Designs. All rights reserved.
